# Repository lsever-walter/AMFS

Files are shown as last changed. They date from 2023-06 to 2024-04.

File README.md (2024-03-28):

# Active Magnetic Field Stabilization
Our goal is to generate magnetic fields on the order of 3 Gauss and to stabilize these magnetic fields to within a signal-noise ratio of $10^3$ for longterm drift (over the course of hours to days) and for 60Hz harmonic noise. This magnetic field stabilization scheme will improve stability for experiments that rely on (near) constant magnetic fields.

## Table of Contents
- [Motivation](#Motivation)
  - [Zeeman Sublevels and Fine Structure](#Zeeman-Sublevels-and-Fine-Structure)
  - [Zeeman Effect](#The-Zeeman-Effect)
- [Components List](#Components-List)
- [Schematics and Components](#Schematics-and-Components)
  - [Experimental Setup](#Experimental-Setup)
  - [Moku Go](#Moku-Go)
  - [N Channel MOSFET](#N-Channel-Mosfet)
  - [Helmholtz Coils](#Helmholtz-Coils)
  - [Magnetometer](#Magnetometer)
- [Feedback Control](#Feedback-Control)
  - [PID Controller](#PID-Controller-(Moku-Go))
  - [Tuning Controller](#Tuning-Controller)
- [Feedforward Control](#Feedforward-Control)
  - [Line Triggering](#Line-Triggering)
  - [60Hz Harmonic Cancellation](#60Hz-Harmonic-Cancellation)
- [Combined Feedback Feedforward Control](#Feedback-and-Feedforward)
- [Two Probe Stabilization with Qnimble and LNA](#Two-Probe-Stabilization-with-Qnimble-and-LNA)
  - [Two Probe Setup Guide](#Two-Probe-Stabilization-Setup-Guide)
  - [Two Probe Data](#Two-Probe-Stabilization-Data)
- [Future Work](#Future-Work)
- [Repository File Structure](#Repository-File-Structure)
- [Contributors](#Contributors)

# Motivation

## Zeeman Sublevels and Fine Structure
<div align="center">
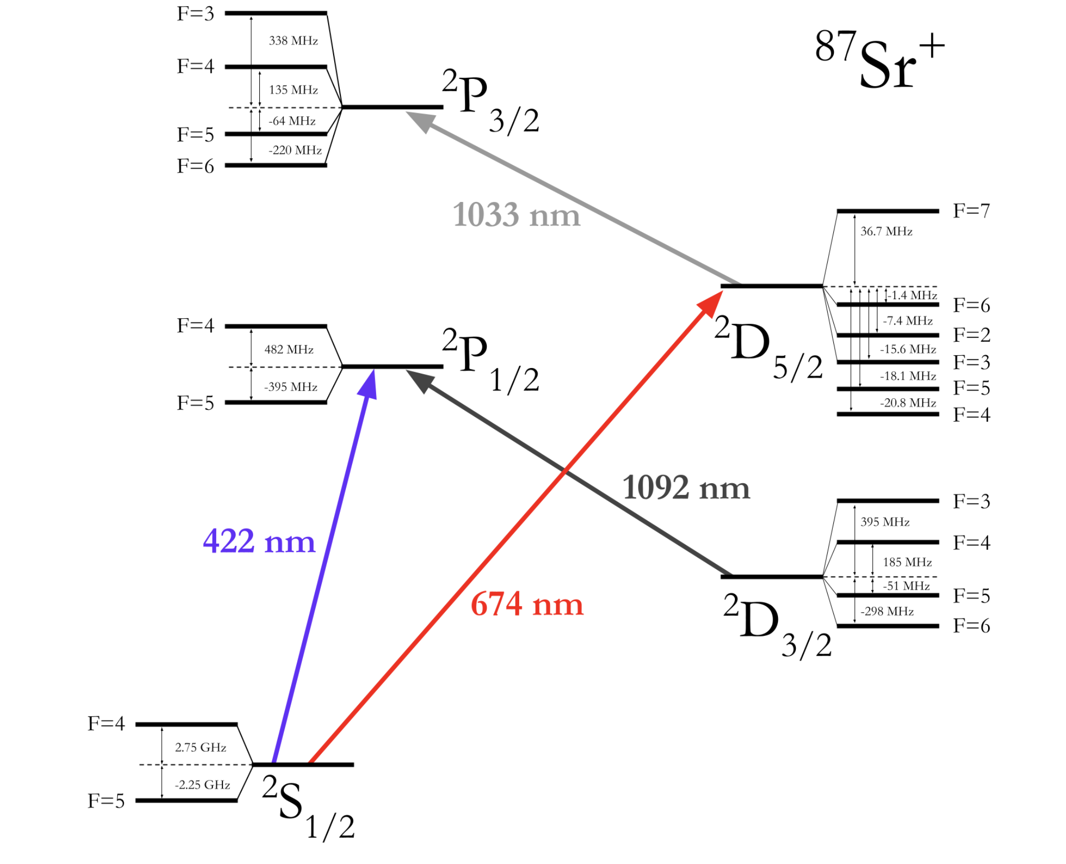
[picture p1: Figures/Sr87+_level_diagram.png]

</div>

In many physics groups investigating the interaction between light and matter use single, or few, atoms confined to a "trapping region." Lasers can drive electronic transitions between energy or angular momentum levels in atoms to investigate their internal structure and to run atomic clock and quantum logic experiments. Pictured above is the level structure of a Strontium 87 ion whose different orbitals experience further splittings for slight changes in the transition frequency which are called "Zeeman Sublevels." Often, exciting transitions between particular Zeeman sublevels is advantageous for certain experiments due to the long lifetimes of the excited state and narrow laser frequencies required to drive the transtion.

## The Zeeman Effect

Unfortunately, ambient magnetic fields in the laboratory can shift the Zeeman Sublevels of an atom during the course of an experiment causing a loss in precision and failure of an experiment. Therefore, to run many atomic and molecular optics, or AMO, experiments it is vital to stabilize the magnetic field experienced by the confined atoms or molecules against ambient magnetic field noise. The goal of our project was to generate and stabilize a 3 Guass magnetic field against slow and fast magnetic field drift as well as the 60Hz harmonics from the mains electricity.

# Components List

1. [MOKU:Go](https://www.mouser.com/ProductDetail/Liquid-Instruments/MOKUGO-M2-WHITE?qs=XAiT9M5g4x%2FfNk%2F%252BrYDr5A%3D%3D&mgh=1&gclid=CjwKCAjw-IWkBhBTEiwA2exyO_NAC4Yzw-N6Kk_8Ar5idSuqgZzDE3XjnfIC7eEdjNcVtmOxlln81RoCZbEQAvD_BwE) - Microcontroller to act as Oscilloscope, PID loop, and AWG
2. [MOSFET N Channel](https://media.digikey.com/pdf/Data%20Sheets/ST%20Microelectronics%20PDFS/2N7000,%202N7002.pdf) - Transistor with input pin, and sends current from drain to source pins
3. [OPAMP LM358AP](https://www.digikey.com/en/products/detail/texas-instruments/LM358AP/379836?utm_adgroup=Texas%20Instruments&utm_source=google&utm_medium=cpc&utm_campaign=PMax%20Shopping_Supplier_Texas%20Instruments&utm_term=&utm_content=Texas%20Instruments&gclid=CjwKCAjw-IWkBhBTEiwA2exyO5folY13R_LqYqakT_OlBMVobZKeyYGEDrK9Rew3klFTzHKU20AtqRoCejcQAvD_BwE) - Low Noise OP AMP 
4. [Bartington Magnetometer](https://www.bartington.com/products/high-performance-magnetometers/mag-03-three-axis/) - reads magnetic field 0-10G, 3kHz bandwidth 
5. [Oscilloscope DS1064](https://www.tequipment.net/RigolDS1064B.html) - with option to AC line trigger

# Schematics and Components

## Experimental Setup

<div align="center">
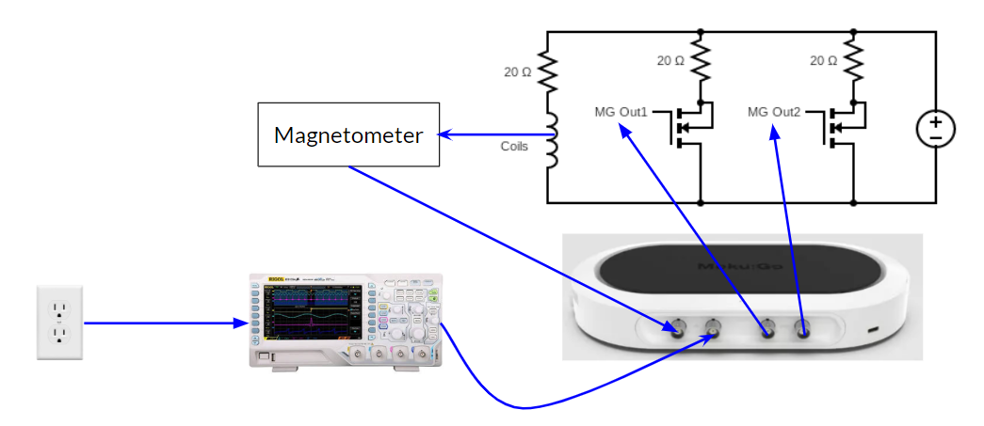
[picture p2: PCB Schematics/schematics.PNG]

</div>

Our Experimental Setup consists of two coils which produce the Helmholtz Field at the center (in our case, 3G). The magnetometer is placed at the center of the coils, and the voltage reading is sent to the Moku:Go controller. The controller is connected to a laptop on which we use the Moku software to run the PID loop and control its parameters. The PID loop output error signal is sent to the first shunt transistor on the bread board (see [Future Work](#Future-Work) for our plans to optimize the circuit on a pcb), "MG Out1" in the diagram above, that shunts current from the coils to alter the magnetic field. Simulatenously, an oscilloscope is used to line trigger a TTL signal on the 60Hz AC line from the wall outlet which is input to the Moku:Go and is used to trigger the Moku:Go Arbitrary Waveform Generator (AWG). The AWG signal is sent to the second shunt transistor, "MG Out2", which is used for feedforward.

## Moku Go
<div align="center">
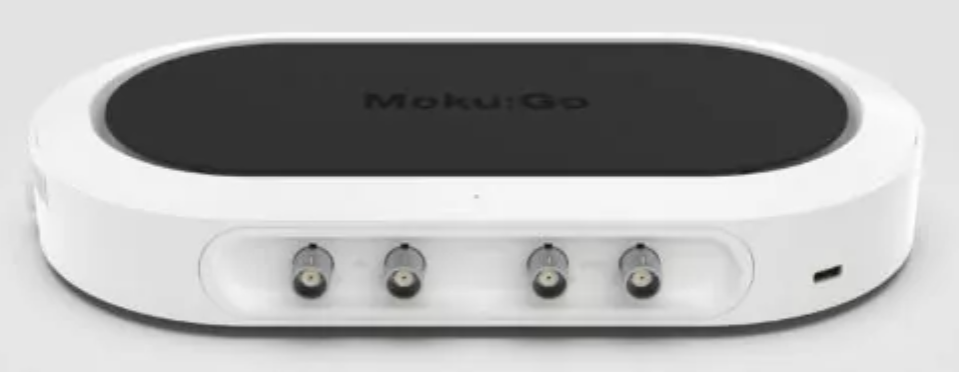
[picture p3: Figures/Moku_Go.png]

</div>

The Moku:Go is a multi-instrument controller that has high sensitivty, sample rate, and output rate which made it ideal to use for this project. The Moku:Go acted as an oscilloscope for the voltage readings from our magnetometer and processed those readings in its PID Controller that was used to generate the feedback error signal. The Moku:Go also had a built in Artbitrary Wave Form generator with which linear combinations of sin waves of different frequencies, amplitudes, and phases could be output and with which feedforward was accomplished. All of our data was also logged using the Moku:Go data logger instrument which has high sample rate and resolution. The Moku:Go power supplies were not used since constant current mode could not be reliably achieved to output .5A to our coil circuit since the impedence of the circuit exceded 5V.

## N Channel Mosfet
<div align="center">
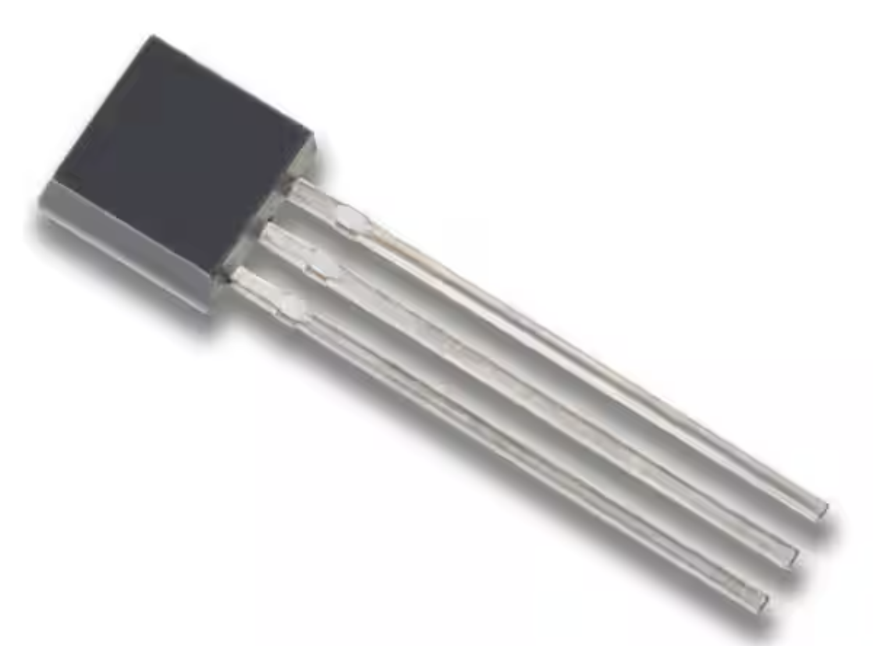
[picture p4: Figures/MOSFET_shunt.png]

</div>

We used an N Channel Depletion Type MOSFET as our shunt transistor to control the current flow through the coils. The MOSFET is a "Metal Oxide Semiconductor Field Effect Transistor" which  changes its resistance been its source and drain pins in response to an applied voltage to its gate pin. The MOSFET(s) were placed in parallel with the coils and the error signal from the Moku:Go was output to their drains to modulate their resistance and consequently the current passing through the coils to do feedback and feedforward control.

## Helmholtz Coils
<div align="center">

</div>

Coils in a Helmholtz Configuration were used for this project due to the stability of the magnetic field in the center of the coils. The coils were placed in series so that the magnetic field pointed in the same direction along the quantization axes parallel to the magnetometer and perpendicular to the plane of the coils with a magnitude $B=(\frac{4}{5})\frac{\mu_{0}NI}{a}$. The resistance of the coils used was on the order of $.3\Omega$ which meant that driving a total current of .25A through our circuit and >.1A through the coils resulted in a 3G magnetic field.

## Magnetometer
<div align="center">
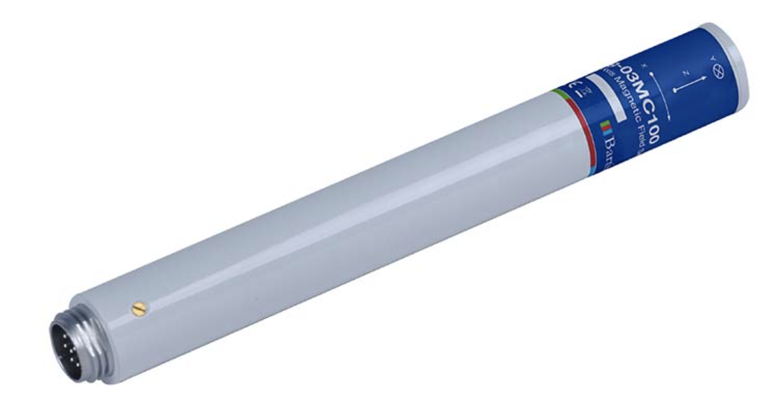
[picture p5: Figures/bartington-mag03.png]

</div>

The magnetometer used in this project was a Bartington Mag-03 fluxgate magnetometer that had a sensor bandwidth of 3kHz and a measuring range of .7 to 10G. The sensor noise floor is <6pTrms per $\sqrt{Hz}$ at 1Hz and offered excellent resolution required for precise PID feedback control. The magnetometer output a voltage signal with a 1:1 ration between volts and gauss to the Moku:Go which applied the PID controller to it. In the future, this magnetometer's ability to sense along three sepperate axes could allow for active magnetic field stabilization along three quantization axes or to sense a magnetic field gradient along one axes. 

# Feedback Control

Our feedback loop consists of a magnetometer, a PID loop in MOKU:Go, and a MOSFET in parallel to the coils shunting current to ground to modulate the field. 

The Bartington Magnetometer is placed at the center of the coils, and sends its reading to the first input pin of the MOKU:Go. The voltage to field ratio of the magnetometer is 1V/G. This is sent to the MOKU's PID loop, where we varied the P and I parameters to reduce the standard deviation as much as possible. The D term was not used as this ended up saturating the PID loop once the external magnetic field became too high. We tuned the parameters to optimize for long term drift cancellation, so Feedforward could handle the faster moving deviations. 

The output of the PID loop was a signal that we sent into a Non-Inverting Amplifier, then to the MOSFET in parallel with our coils. 

The NonInverting Amplifier circuit consisted of an OpAmp, two resistors, and a capacitor. The circuit is below, and the gain of this circuit is 6. The purpose of this circuit is to set the input of the MOSFET in the middle of its range of 0-60 volts. We would then have more control on how much it attenuates the signal. 

<image src="https://github.com/lsever-walter/AMFS/assets/125600843/0734a2d0-c5d2-4a97-9a83-c12c311680be">
 
The output of this circuit was sent to the MOSFET to shunt current accordingly to ground.

## Tuning Controller
<div align="center">
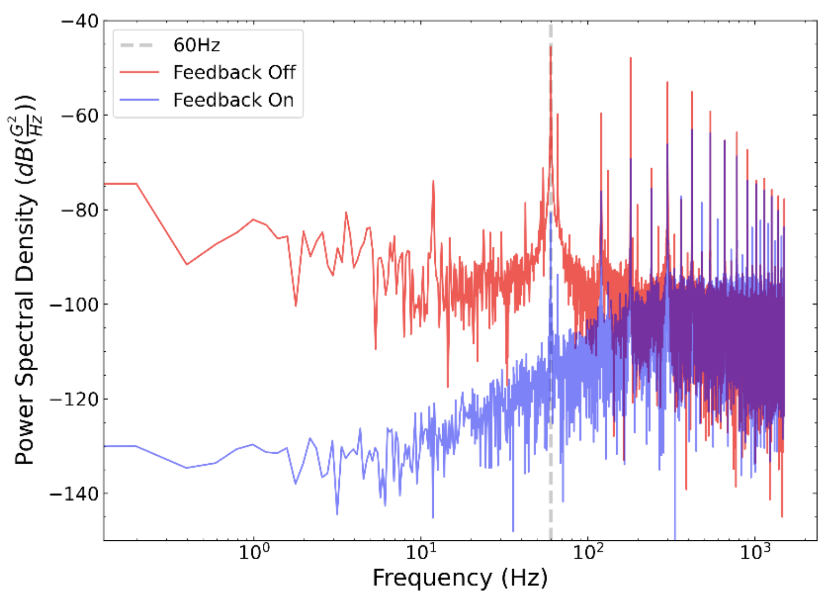
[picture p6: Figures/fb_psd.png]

</div>
When the PID feedback was off, there were significant noises in our magnetic field signal that were mostly composed of 60 Hz harmonics. As the feedback was enabled, the standard deviation decreased from 3.9 mG to 0.8 mG. We observed a distinct attenuation of power in small frequencies range of our FFT plot. However, there still remained 60 Hz harmonics peaks that are slightly reduced by PID feedback. By integrating the power spectral density over frequencies from 0 to 300 Hz, above which the PID feedback ceases to effect, we obtained an area ratio of 163.

# Feedforward Control

Feedforward control consists of modifying the input to the system by modulating the source of the disturbance. In this case, the disturbance is the 60Hz from the powerwall that leaks through the DC power supply, as well as 60Hz that enters the magnetic field from laptops and other devices that run at 60Hz. 

Our feedforward methology relies on finding the phase of the 60Hz sin wave in the magnetometer and shunting current to decrease the amplitude of this singal.

## Line Triggering

We AC line triggered from DS1064 Oscilloscope, and produced a TTL (time-to-live) at this frequency and sent this to the Moku:Go. The Moku's AWG produced a sin wave at this frequency. We set the period of this sin wave to be slightly more than 60Hz (~60.05 Hz), so that any error in the TTL's phase did not affect the AWG's produced sin wave.

We then obtained the signal from the magnetometer, and sent this into the MOKU:Go in multi instrument mode. We then phase shifted the sin wave produced by the Moku to be in phase with the 60Hz wave in the magnetometer reading. We then sent the in phase sin wave from the AWG to the second MOSFET in our circuit to shunt away current at this frequency to attenuate 60Hz in the magnetic field.

As a result, the 60Hz in the magnetic field was attenuated. 

## 60Hz Harmonic Cancellation
<div align="center">
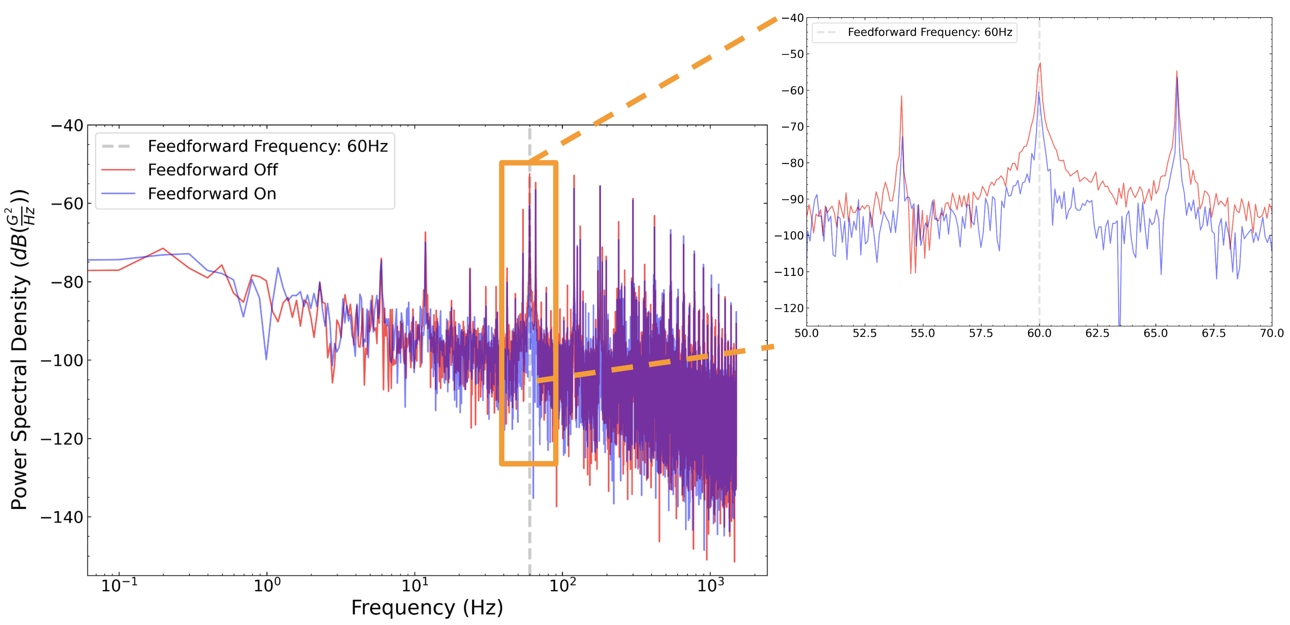
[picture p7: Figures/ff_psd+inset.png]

</div>
The power spectral densities over frequency corresponding to cases of feedforward on and feedforward off are nearly identical, as what we have expected. This is because we were outputing a 60 Hz sinusoidal wave that is in phase with the magnetometer signals, the rest of the spectrum should, therefore, be highly similar. As we zoomed into the region of interest (f = 60 Hz), we observed an approximaely 8 dB attenuation at 60 Hz by subtracting the peaks to their respective noise floors, which are about the same in this case. 

# Feedback and Feedforward
<div align="center">
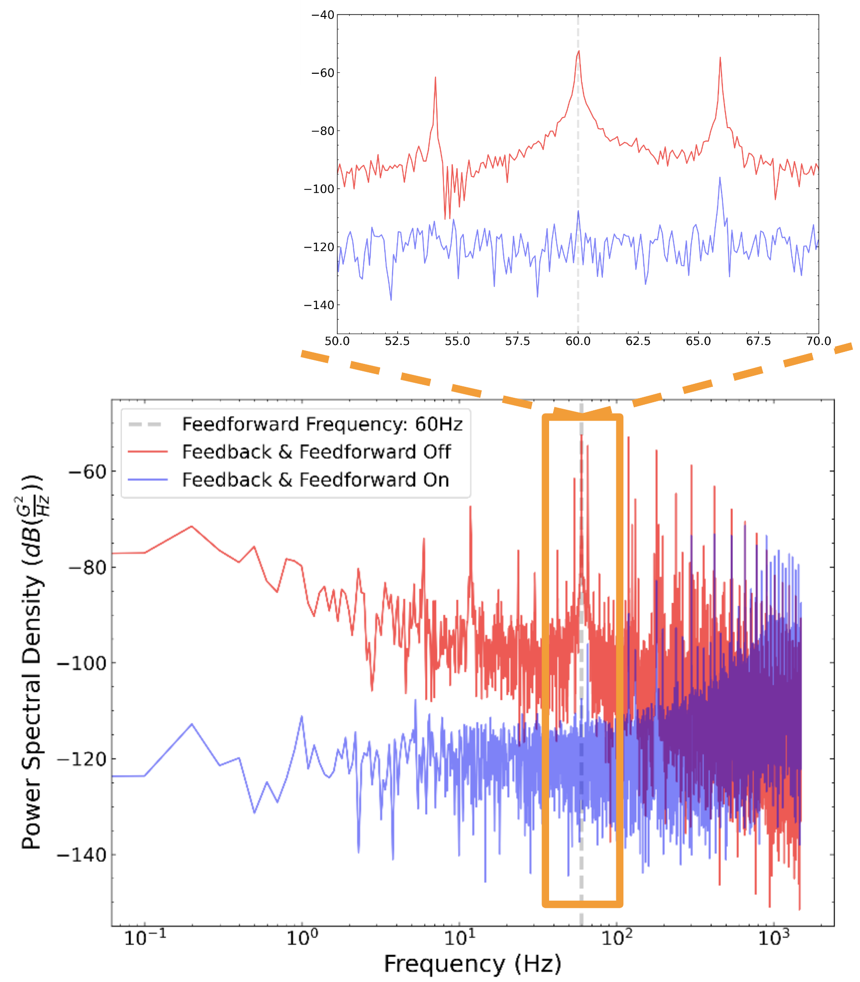
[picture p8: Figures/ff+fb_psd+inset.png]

</div>
After the individual implmentation of PID feedback and mains electricity feedforward, we combined both methods to further attenuate the noises in our signal. The standard deviation was reduced to 0.4 mG, as contrast to 0.8 mG for PID feedback alone. There was about 35 dB attenuation of power spectral density at 60 Hz, from which we obtained by subtracting the peak value at 60 Hz from their respective noise floors. Through integrating the power spectral density to the bandwidths of PID feedback alone (f = 300 Hz) and of Feedback and Feedforward (f = 850 Hz), we calculated area ratios of 705 and 65, respectively.

# Two Probe Stabilization with Qnimble and LNA

## Two Probe Stabilization Setup Guide
1. The moku:go will be used for live measurements so you can tune things more quickly, the Qnimble is what’s actually used as the PID controller. 

2. Two BNC connectors go from the two magnetometer output ports that are being used to the LNA setup with the breadboard. Each BNC coming from the magnetometer should have a BNC to banana adapter on the end. The grounds of the banana adapters should be connected. The positive side of the banana adapters should go into the breadboard’s banana connector slots, one into the breadboard’s ground (green female end banana connector on the breadboard) and one into the breadboard’s Vb (black female end banana connector on the breadboard). 
3. Current then travels through those two ports and then each through its own 10k resistor. After current passes through each respective 10k resistor, there is a junction that then goes to the breadboard’s Va (red female end banana connector on the breadboard). 
4. The LNA’s input port should have a BNC to banana adapter on it, and you should put a banana cable (preferably red) from the breadboard’s Va connector to the positive terminal of the LNA. There should be another banana cable (preferably black) going from the ground of the magnetometer signals (it doesn’t matter which you connect it to since they should be connected to each other already)
5. The output of the LNA is split with one end into the moku’s input and one into the Qnimble’s input.
6. The LNA is a current amplifier, but we want to amplify a voltage, so we put resistors out front. It should be such that the resistors are quite high because we don’t the magnetometers to have to output much current at all. V=IR tells us that the current read will be I=V/R, so with 10k resistors like I’ve used, the current read by the LNA will be 1e-4 in amps of the voltage going in. For example if I supplied one volt, I would have 100uA being read by the LNA. Because I have two ~1V signals (for a 1 gauss field read by each probe) coming in from each magnetometer output, they will each turn into 100uA of current, and by the junction rule that current adds to 200uA when it goes into the LNA input, so it will read 200uA. There should be no concern about back flow of current because the LNA has very nearly zero resistance and the back flow path requires the current to flow through an extra 10k ohm of resistance, so the backflow current should be pretty much zero.
7. Because we have 10k resistors out front, set preamp to -200uA input offset. Be careful to make sure that you have the negative mode selected. Input offset depends on the resistors used, and -200uA is corresponds to zeroing the current of 2 signals each of 1V (for 1 gauss as read by each magnetometer probe) coming in. Have the preamp gain set to 100mA/V for tuning (this LATER gets increased to 200nA/V once you zero the center the fluctuating B field reading about 1G for each probe)
8. Turn on the op amp and circuit power supplies, OP Amp gets 20-30V, circuit pwr gets ~0.2A to start (you will vary this to get an LNA reading centered about zero). 
9. With the circuit pwr, the power supply needs to have its current limit set to output at a fixed current as opposed to a fixed voltage, so set that limit to 0.2A and that in the later steps to control the current. 
10. Turn on the LNA and view the LNA’s output in the moku:go desktop app with the Qnimble’s DAC offset set to ~0.4V.
11. Vary the circuit pwr current until the moku:go shows the signal as closely centered about zero as you can get, this means the field read by each magnetometer probe is 1G
12. Now increase the gain on the LNA to 10uA/V, repeat step 11 if the center of the signal changes from zero.
13. Now increase the gain once again to 1uA/V, again repeat step 11 if needed (best to get the signal as near as possible to centered about zero). You may also need to vary the DAC offset in the Qnimble applet for more fine tuning to get the LNA output centered about zero.
14. Now increase the gain on the LNA to the final level of 200nA/V and again tune the DAC offset to get it as nearly centered about zero as possible. 
15. Now it’s ready for testing the stabilization performance.
16. Note that this is very finely tuned for whatever setup you have it set to, so if you move a magnet within the vicinity or move a current carrying wire within the vicinity, you likely will have to re-calibrate by adjusting the DAC output offset in the Qnimble applet again.
17. Here are some parameters have performed well in tests:
P=0.0005, I=0.05, D=0, SP=0, DAC=0.414
The optimal DAC (DAC offset) value will probably differ, see the above setup guide for proper DAC tuning.

## Two Probe Stabilization Data

<p align="center">
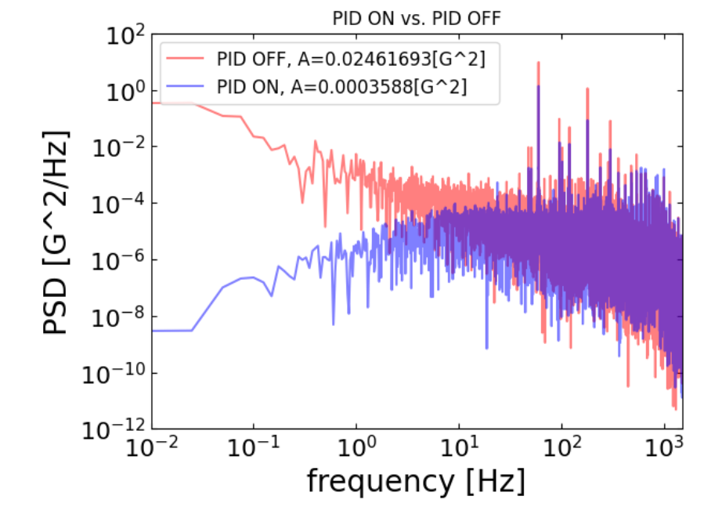
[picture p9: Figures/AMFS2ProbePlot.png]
hover text
  
</p>

Note that this plot did not use feedforward or a direct attenuation of the 60Hz noise, this plot is only to showcase the ability to attenuate low frequency noise with the Qnimble Quarto as a controller, an SRS LNA to amplify the signal, and B field probes whose measurements are fed into a passive averager circuit to allow for two probe stabilization. This data was recorded for the PID parameters suggested in the setup guide. Many sets of parameters were tested, but this plot represents the most significant reduction in low frequency noise without significant overcorrection noise at higher frequencies. There is a small overcorrection hump that peaks at ~1kHz, but it is at roughly 1/1000 the noise levels of the low frequency noise that has been attenuated. 

# Future Work
For our future work we hope to implement the stabilization setup developed above on a linear paul trap. We hope to first move optimize our circuits with voltage regulators to protect the operation amplifiers and coils from DC current spikes that could damage the circuitry and potentially the magnetometer. We would then like to implement feedforward for further 60Hz harmonics to attenuate up to 240Hz which would likely increase our PID bandwidth as well. Finally, we would then aim to implement our setup on a linear paul trap by designing new coils to it the ion trap geometry and then use the ion itself to quantify the magnetic field stability in addition to, or perhaps instead of, the magnetometer. 

# Repository File Structure
  
All of the analysis and plotting of our data was done in python and the code used along with the plots included in this README are in the `AMFS/Analysis_code` subdirectory. The raw data is saved in CSV file format in the `AFMS/Data` subdirectory and can be used to reproduce or customize the included plots. The PCB schematics for the circuit board we want to use in the future have been included in the `AMFS/PCB Schematics` folder, however these were not used for this project and have not been tested. We have also included a pdf of our final presentation for this work in the `AFMS/Presentation` subdirectory. All schematics, photographs, and figures appearing in this README are stored in the `AMFS/Figures` folder. Finally, we included test scripts made public by liquid instruments to help with trouble shooting the Moku python API in the `AMFS/Controller` folder. This code was not used for this work but may be useful in the future should we want to switch to the Moku python API instead of the Moku Desktop App. 
  
# Contributors
This work was primarily done by Luka Sever-Walter, Xuanwei Liang, and Samyuktha Ramanan for 15CL at UCSB.

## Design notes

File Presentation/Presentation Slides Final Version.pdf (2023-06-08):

# Active Magnetic Field Stabilization

# Luka, Samyuktha, Xuanwei

# PHYS 13/15C Final Presentation

6/5/23

# Why Stabilize?

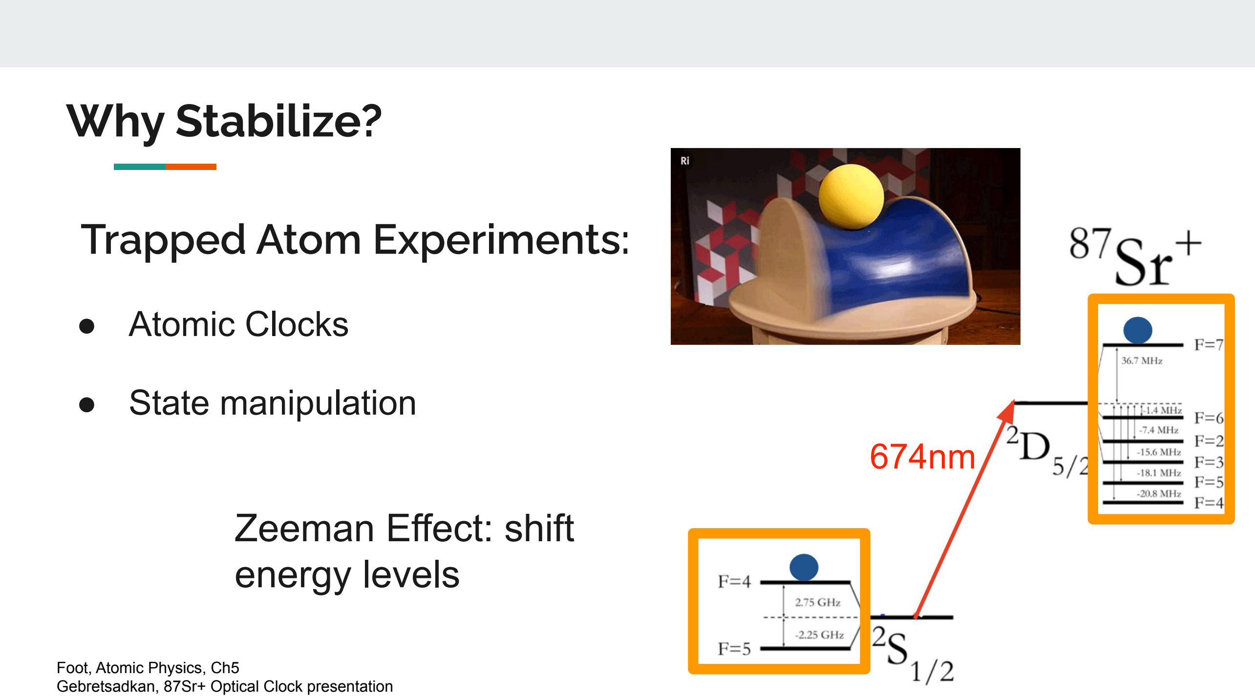
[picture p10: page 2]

# Trapped Atom Experiments:

# Zeeman Effect: shift energy levels

674nm

# - Atomic Clocks

# - State manipulation

Foot, Atomic Physics, Ch5
Gebretsadkan, 87Sr+ Optical Clock presentation

# Generating Helmholtz Field

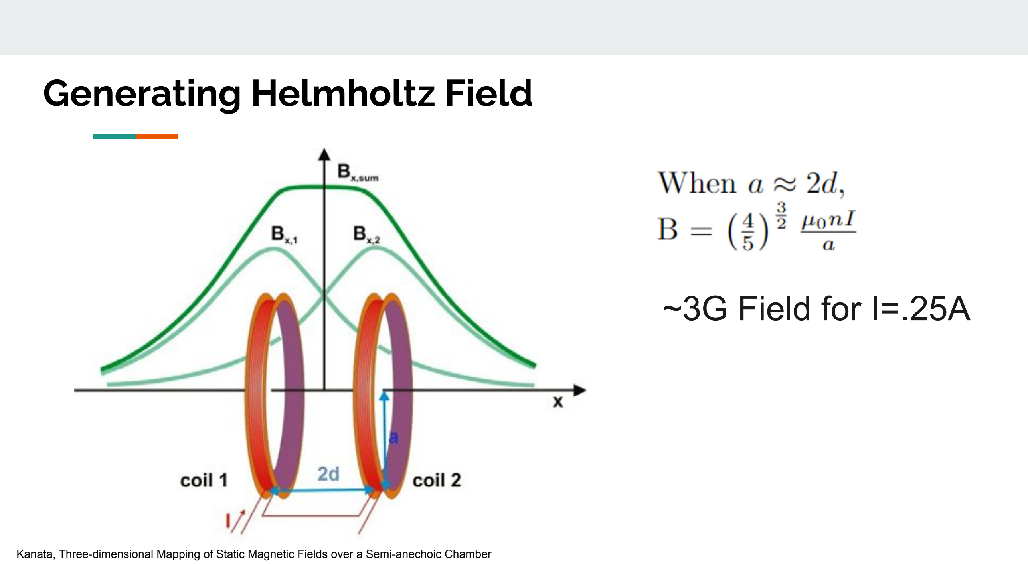
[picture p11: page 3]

# ~3G Field for I=.25A

Kanata, Three-dimensional Mapping of Static Magnetic Fields over a Semi-anechoic Chamber

# Helmholtz Field Drift

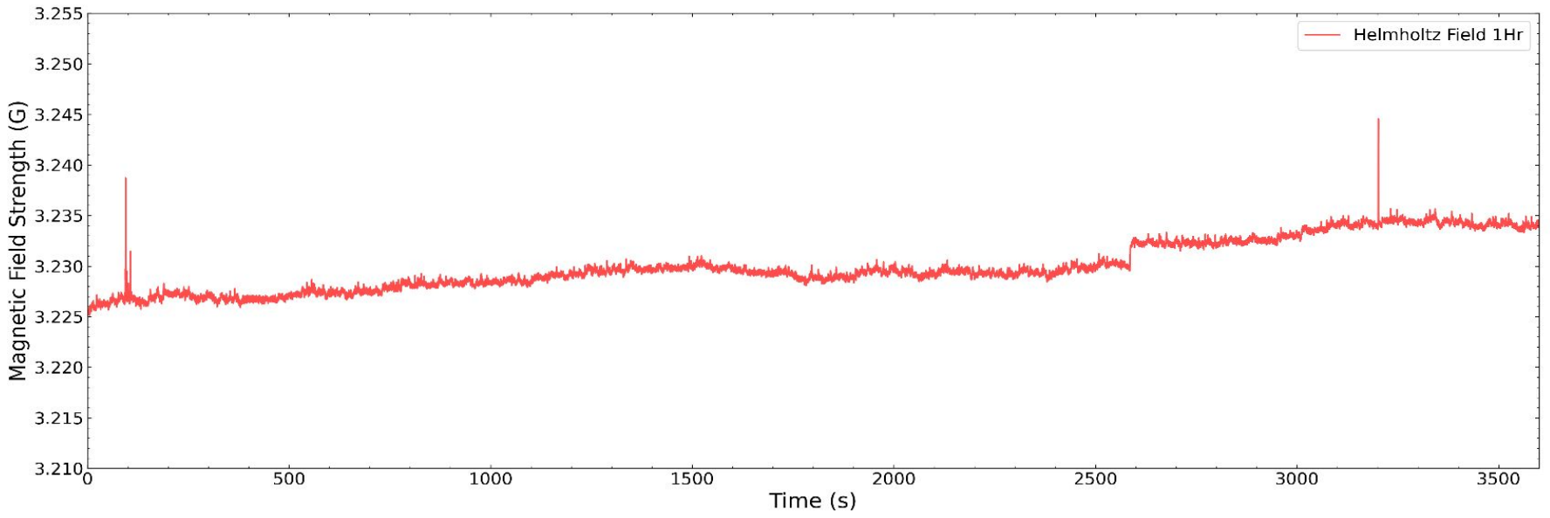
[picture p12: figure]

# 3600s Drift:

3.2300 ± 0.0025G

# 10s Drift

3.1107 ± 0.0017G

# Feedback vs. Feedforward

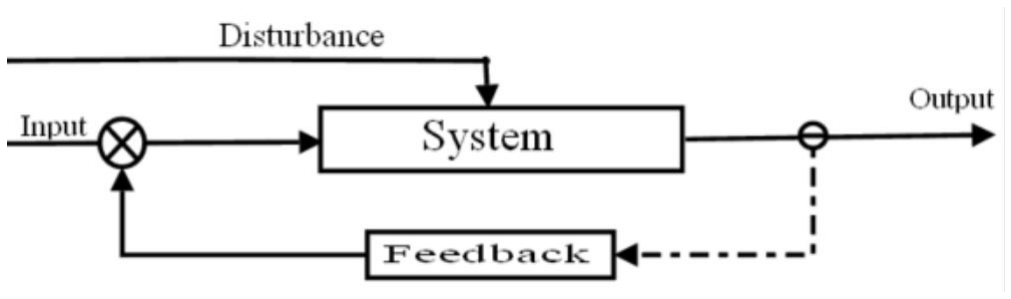
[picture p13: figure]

# - Feedback: modify input based on output

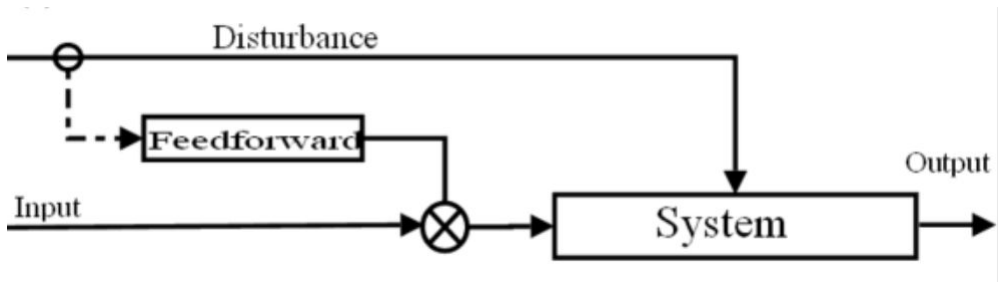
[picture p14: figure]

# - Feedforward: modify input based on external trigger

Merkel, Magnetic field stabilization system for atomic physics experiments, Oxford. Tarlton, Probing qubit memory errors at the 10⁻⁵ level, Imperial College London Fig: Feedforward (control), Wikipedia

# Experimental Setup

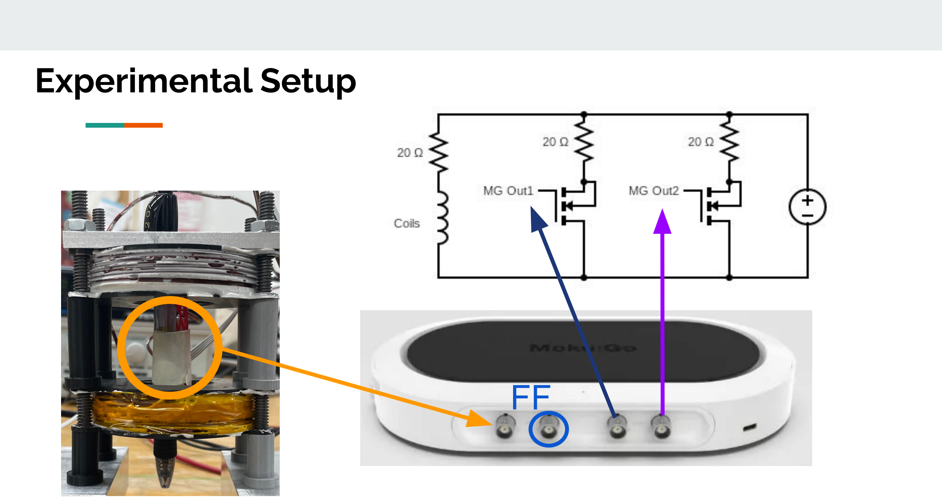
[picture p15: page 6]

FF

# Proportional-Integral-Derivative (PID) Feedback:

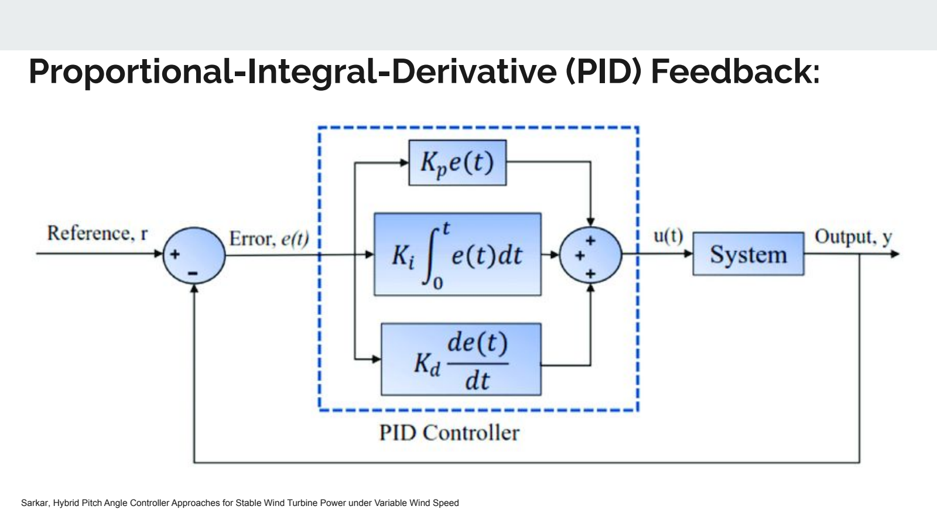
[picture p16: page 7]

Sarkar, (https://www.researchgate.net/profile/Md-Rasel-Sarkar) Hybrid Pitch Angle Controller Approaches for Stable Wind Turbine Power under Variable Wind Speed

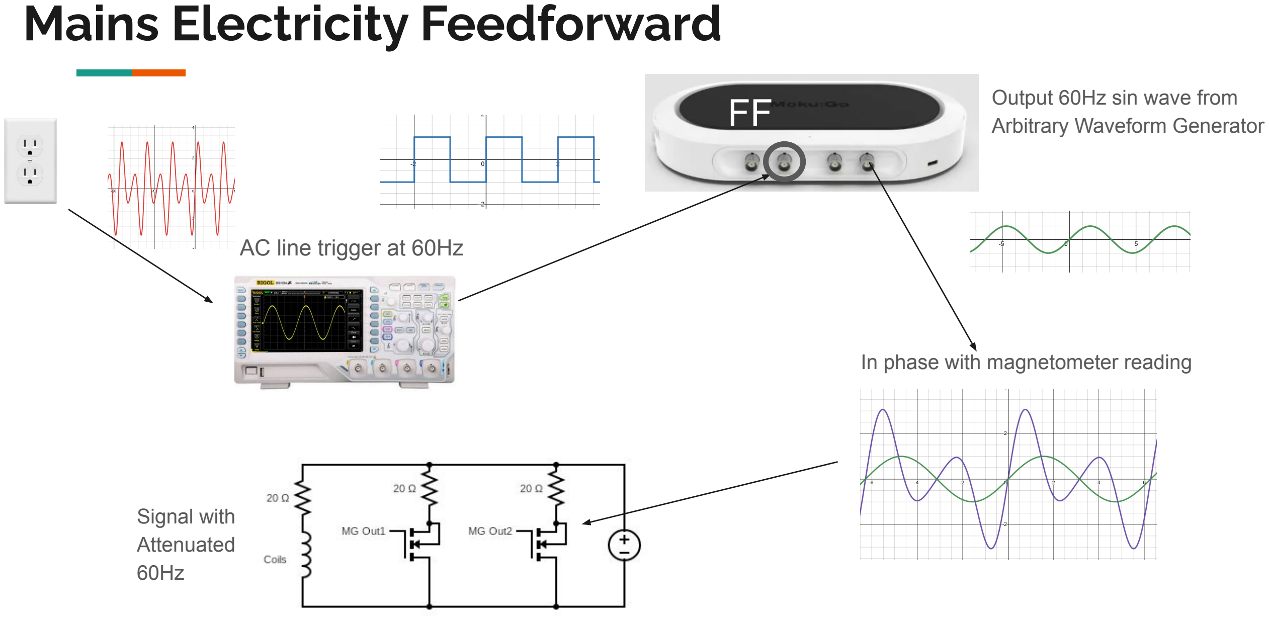
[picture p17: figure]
Mains Electricity Feedforward; AC line trigger at 60Hz; In phase with magnetometer reading; Signal with Attenuated 60Hz

Output 60Hz sin wave from FF | Arbitrary Waveform Generator

# Magnetic Disturbance

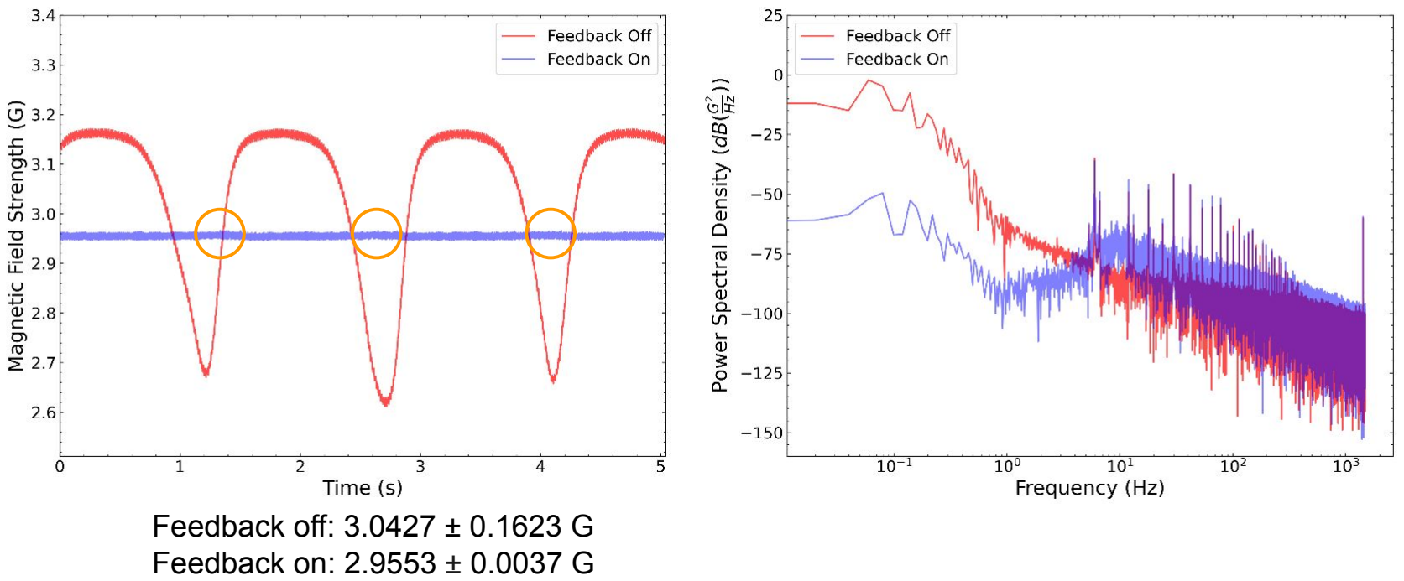
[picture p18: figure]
Feedback off: 3.0427 ± 0.1623 G Feedback on: 2.9553 ± 0.0037 G

# PID Feedback

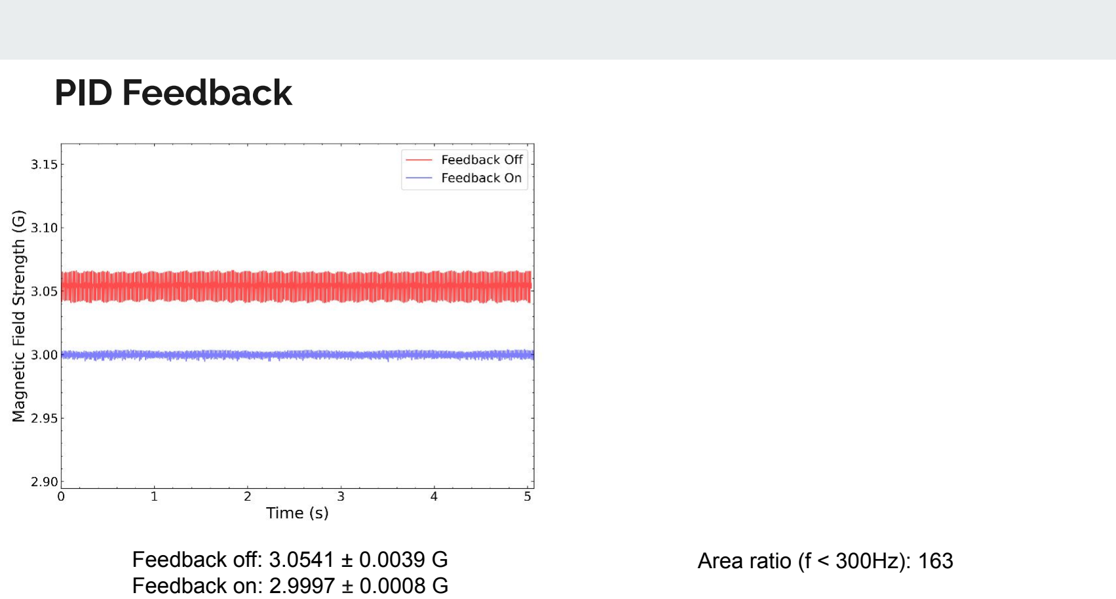
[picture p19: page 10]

# Feedback off: 3.0541 ± 0.0039 G Feedback on: 2.9997 ± 0.0008 G

# Area ratio (f < 300Hz): 163

# Feedforward at 60Hz

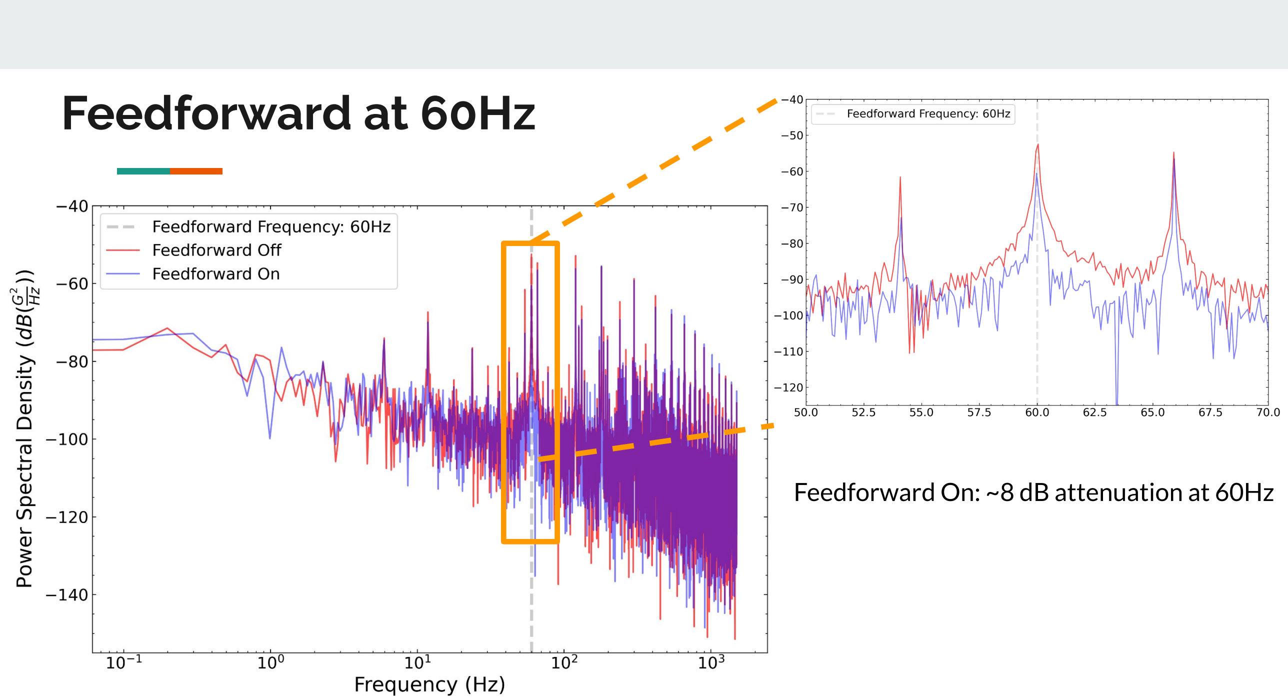
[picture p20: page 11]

# Feedforward On: ~8 dB attenuation at 60Hz

# Feedback and Feedforward

# Area ratio: 705 (f < 300 Hz) & 65 (f < 850 Hz)

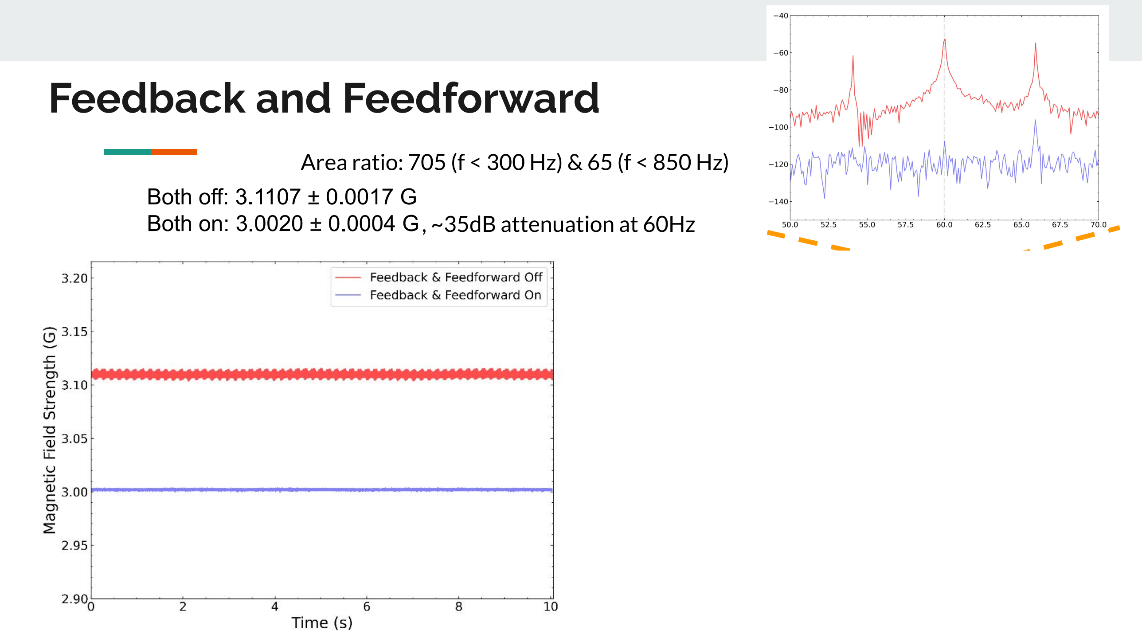
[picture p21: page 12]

# Both off: 3.1107 ± 0.0017 G

# Both on: 3.0020 ± 0.0004 G, ~35dB attenuation at 60Hz

# Conclusion:

| Dominant noise | Noise source
Both off | Slow drift + 60Hz Harmonics | Power supply + Ambient line noise
Feedback alone | 60Hz Harmonics | Ambient line noise
Feedforward alone (60Hz) | Slow Drift | Power supply + Ambient line noise
Both on (60Hz) | 60Hz Harmonics (120Hz or higher) | Ambient line noise

# Future Plans

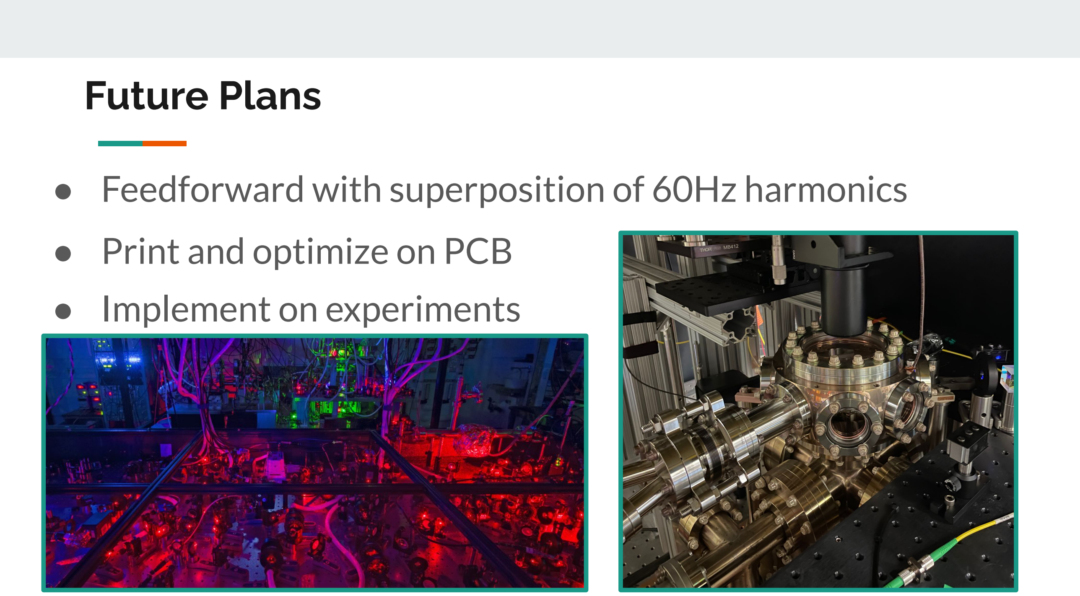
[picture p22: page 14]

# - Feedforward with superposition of 60Hz harmonics

# - Print and optimize on PCB

# - Implement on experiments

# Acknowledgement

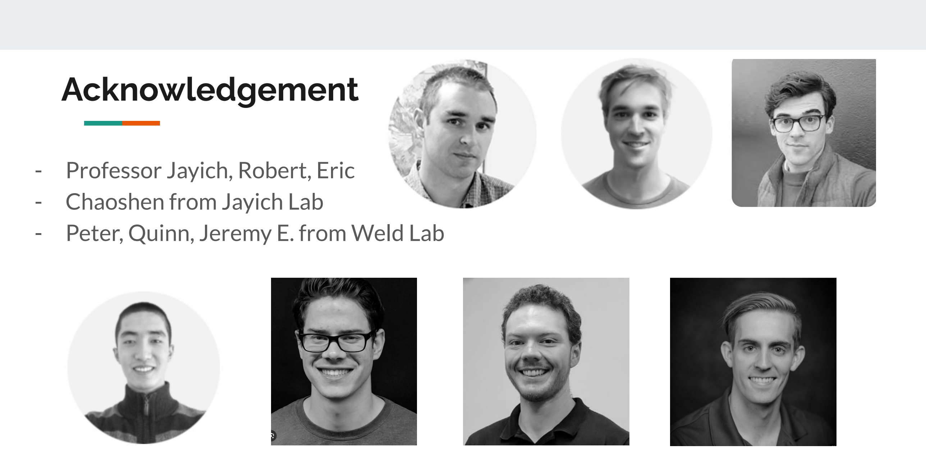
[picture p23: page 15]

# - Professor Jayich, Robert, Eric - Chaoshen from Jayich Lab - Peter, Quinn, Jeremy E. from Weld Lab

# Questions?

# PID Feedback

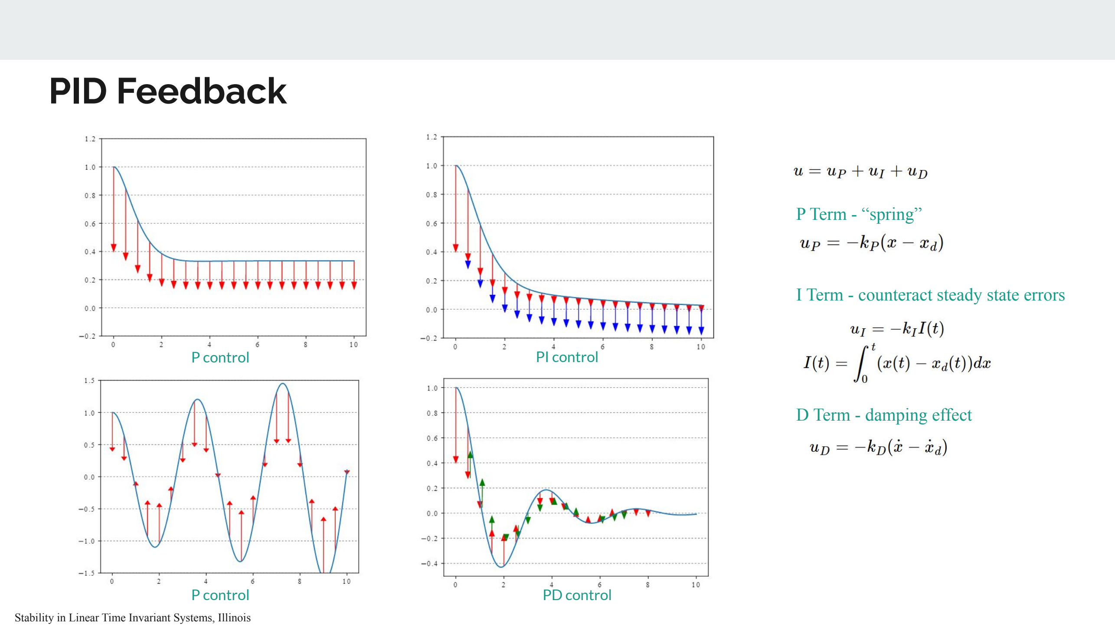
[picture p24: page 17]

### P control

### P control

### PI control

### PD control

## P Term - “spring”

## I Term - counteract steady state errors

## D Term - damping effect

Stability in Linear Time Invariant Systems, Illinois

# Power Spectral Density Derivation

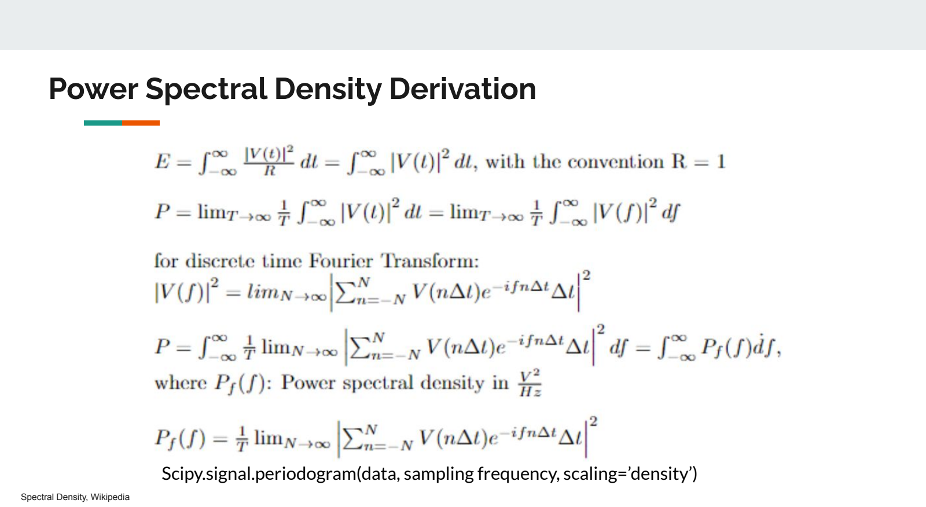
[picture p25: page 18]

# Scipy.signal.periodogram(data, sampling frequency, scaling=’density’)

Spectral Density, Wikipedia

# Bartington-03 Fluxgate Magnetometer

# Data Sheet:

# - Noise levels down to <6pTrms/√Hz at 1Hz

# - Measuring ranges from ±70μT to ±1000μT - Bandwidth 3kHz

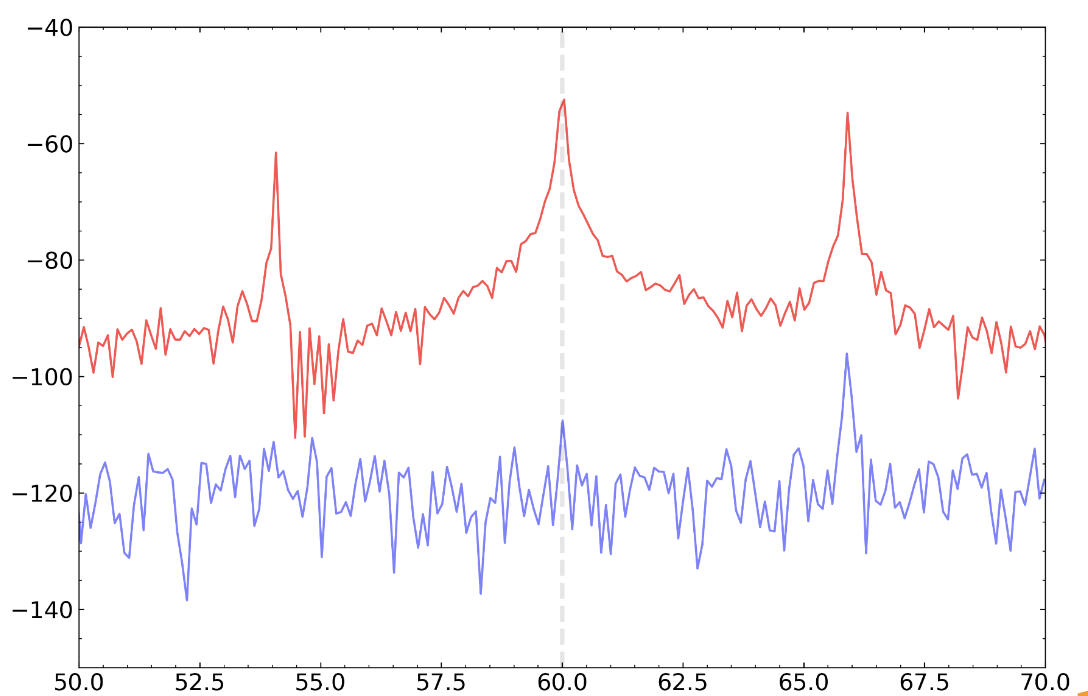
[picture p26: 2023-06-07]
Figures/fb+ff_inset.png

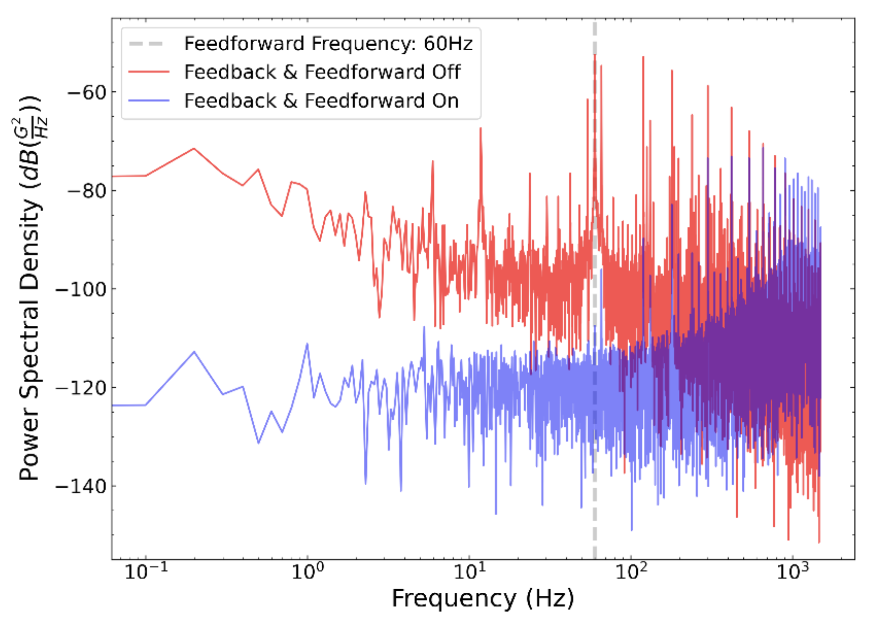
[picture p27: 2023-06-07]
Figures/fb+ff_psd.png

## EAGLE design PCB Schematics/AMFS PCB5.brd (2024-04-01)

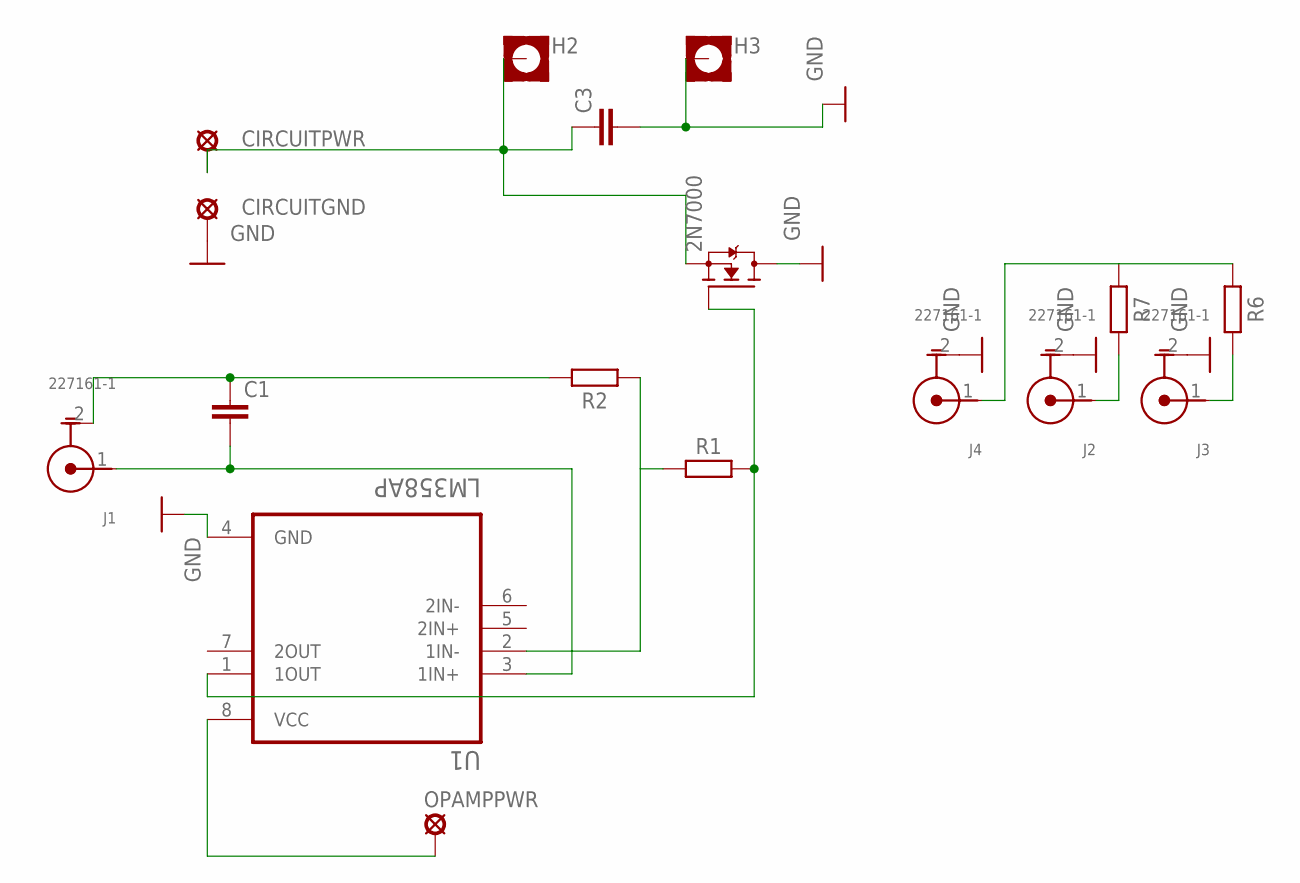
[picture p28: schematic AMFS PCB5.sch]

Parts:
C1, C3: C5/3.5; C5B3.5
CIRCUITGND: MCS10B
CIRCUITPWR: MCS10B
H2, H3: MOUNT-PAD-SQUARE2.8; 2,8-PAD-SQUARE
J1, J2, J3, J4: 227161-1; TE_227161-1
OPAMPPWR: LSP10
R1, R2, R6, R7: R_AXIAL-7.2MM-PITCH; RESAD724W46L381D178B
SHUNT: 2N7000; TO92-
U1: LM358AP; DIP794W45P254L959H508Q8

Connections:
GND: C3.2, CIRCUITGND.MP, H3.B2,8, J2.2 (G), J3.2 (G), J4.2 (G), SHUNT.1 (D), U1.4 (GND)
unnamed: C3.1, CIRCUITPWR.MP, H2.B2,8, SHUNT.3 (S)
unnamed: OPAMPPWR.MP, U1.8 (VCC)
unnamed: C1.2, J1.1 (C), U1.3 (1IN+)
unnamed: C1.1, J1.2 (G), R2.2
unnamed: R1.1, R2.1, U1.2 (1IN-)
unnamed: J2.1 (C), R7.2
unnamed: R1.2, SHUNT.2 (G), U1.1 (1OUT)
unnamed: J3.1 (C), R6.2
unnamed: J4.1 (C), R6.1, R7.1

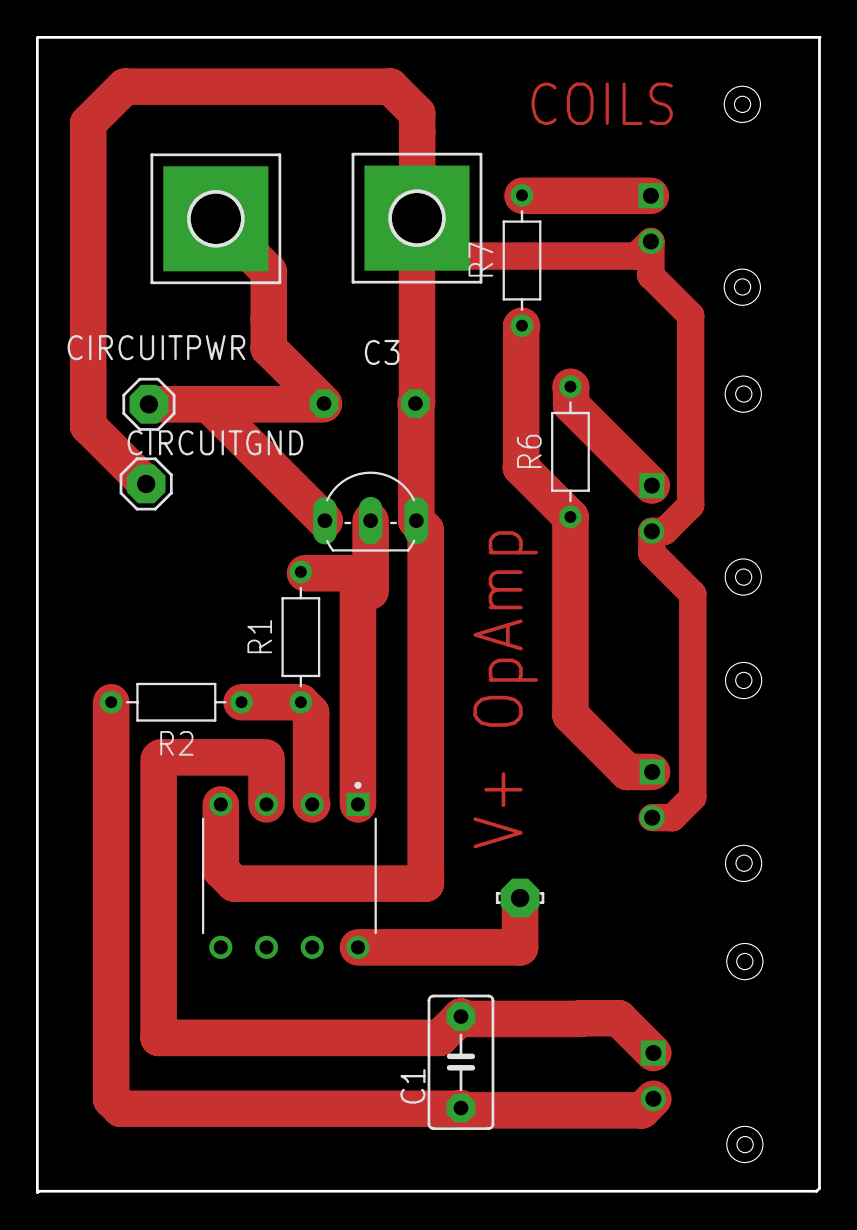
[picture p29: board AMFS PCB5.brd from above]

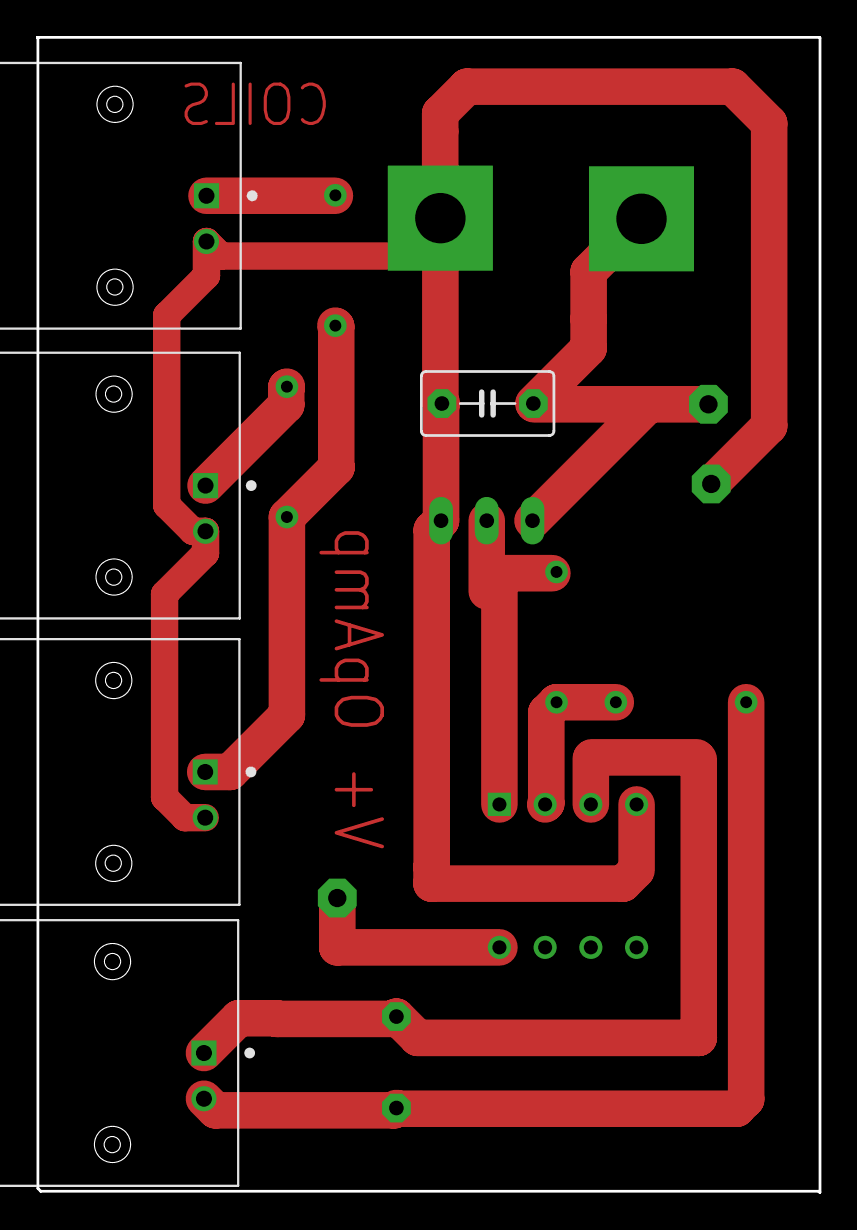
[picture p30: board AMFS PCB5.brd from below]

Board: 2 copper layers, 43.5 x 64.2 mm, 17 parts (5 on the bottom side), 10 nets.

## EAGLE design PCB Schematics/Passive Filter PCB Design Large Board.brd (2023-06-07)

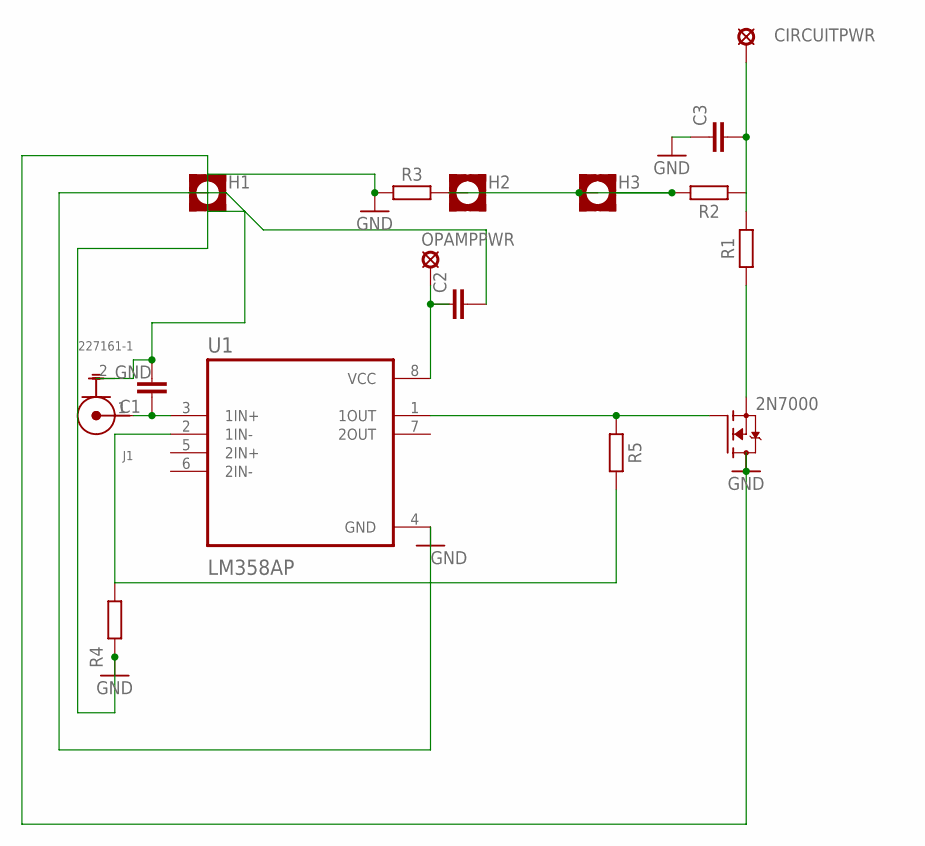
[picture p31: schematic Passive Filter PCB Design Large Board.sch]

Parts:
C1, C2, C3: C5/3.5; C5B3.5
CIRCUITPWR: MCS10B
H1, H2, H3: MOUNT-PAD-SQUARE2.8; 2,8-PAD-SQUARE
J1: 227161-1; TE_227161-1
OPAMPPWR: LSP10
R1, R2, R3, R4, R5: R_AXIAL-7.2MM-PITCH; RESAD724W46L381D178B
SHUNT: 2N7000; TO92-
U1: LM358AP; DIP794W45P254L959H508Q8

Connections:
GND: C1.2, C2.2, C3.1, H1.B2,8, J1.2 (G), R3.1, R4.2, SHUNT.1 (D), U1.4 (GND)
MOKU-IN: C1.1, J1.1 (C), U1.3 (1IN+)
unnamed: R1.1, SHUNT.3 (S)
unnamed: H2.B2,8, H3.B2,8, R2.1, R3.2
unnamed: C2.1, OPAMPPWR.MP, U1.8 (VCC)
unnamed: R5.1, SHUNT.2 (G), U1.1 (1OUT)
unnamed: R4.1, R5.2, U1.2 (1IN-)
V+30V: C3.2, CIRCUITPWR.MP, R1.2, R2.2

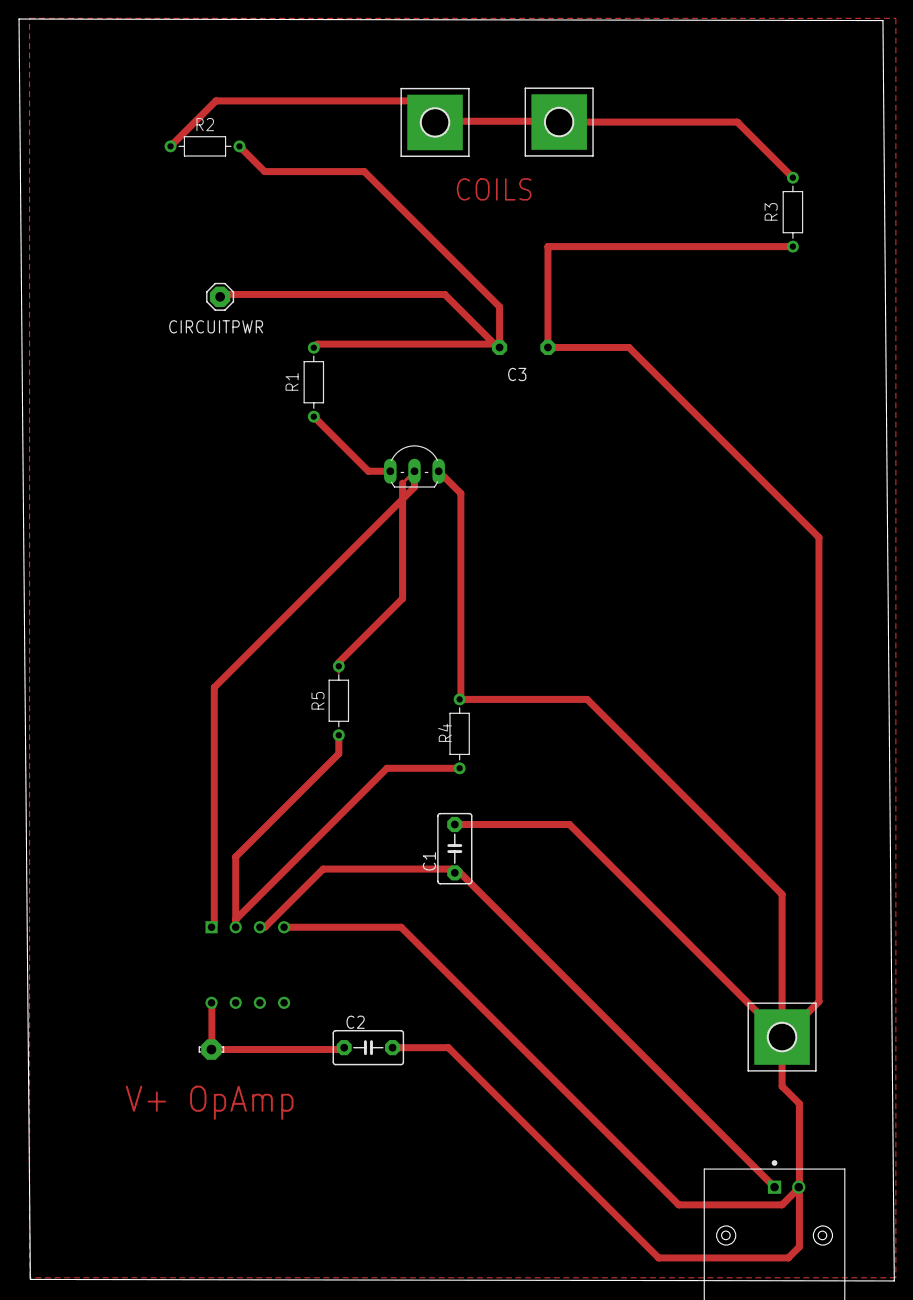
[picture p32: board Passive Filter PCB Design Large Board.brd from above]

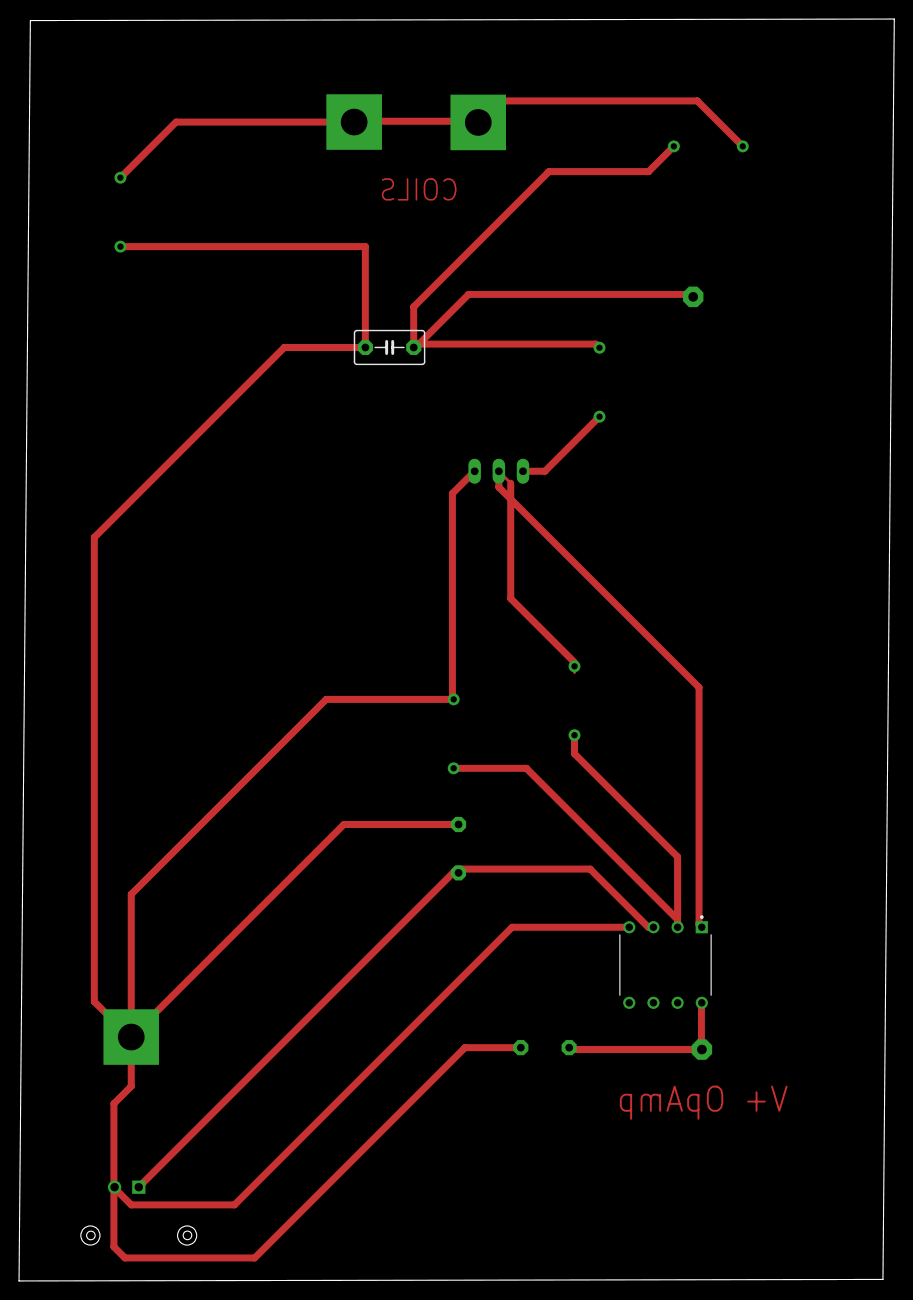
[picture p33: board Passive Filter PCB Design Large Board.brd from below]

Board: 2 copper layers, 91.9 x 132.6 mm, 16 parts (2 on the bottom side), 8 nets.

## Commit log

2023-06-09 Delete AMFS_circuit1.png
    Wrong sign for the battery
2024-03-28 Most recent PCB files
    Flipped op amp, flipped BNCs, removed no longer useful resistors and a capacitor that didn't make much sense, and added LNA passive averaging circuit.
    [AMFS PCB4.brd, AMFS PCB4.sch]
2024-03-28 Latest AMFS PCB
    Includes LNA passive averaging resistors and BNC connectors.
    [AMFS PCB5.brd, AMFS PCB5.sch]
2024-04-01 Add files via upload
    Updated .brd file because it was previously missing the board layout and wouldn't open in the bantam software
    [AMFS PCB5.brd, AMFS PCB5.sch]
